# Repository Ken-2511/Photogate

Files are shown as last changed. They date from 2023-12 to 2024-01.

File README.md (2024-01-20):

# Photogate

## Background

Photogates are used to measure objects' speed or acceleration. My high school physics teacher wanted a teaching aid to demonstrate the objects' speed change. In her imagination, there are ten photogates forming a tunnel, and an object go through the photogates, and the photogates show the time of seeing the object.

## My Design Specification

Here is my design specification.

### How to Detect Object

I decided to use laser emitter and receiver to detect objects' movement. Whenever an opaque object goes through the photogate, the laser is blocked, and the laser receiver would push a signal to the microprocessor (Arduino-nano).

<div align="center">
  
  <p><i>Figure 1. Red laser</i></p>
</div>

### How to Show the Time

I installed a nixie-tube on each photogate to show their time (Figure 1) and the nixie-tube is controlled by an Arduino-nano.

<div align="center">
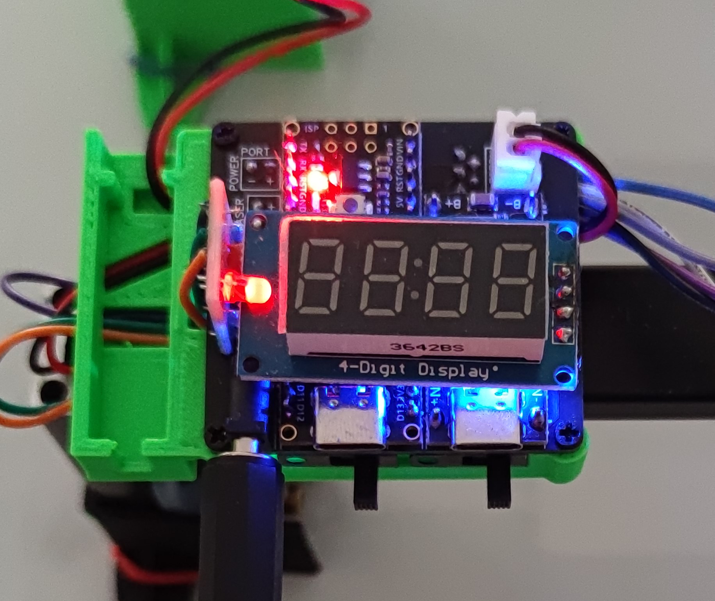
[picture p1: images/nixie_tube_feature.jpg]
  
  <p><i>Figure 2. Nixie Tube</i></p>
</div>

### How to Adjust Time

Since Arduino has no time-adjusting function, and the time-measuring job requires a very precise timing: the time error should be less than 1 millisecond. Thus, we should better not use bluetooth or WiFi to adjust time.

In this project, I used infrared remote controlling technique, similar to TV controller or AC controller.

However, the existing libraries does not fulfill our need as they are memory-consuming and low-efficient. Most libraries only support to transmit 8 bits per time. Therefore, I developed my own "protocol" to allow it transmit up to 32 bytes (256 bits) per time (they are defined in "photogate.c" and "PhotogateController.c").

There is a "photogate controller", as the name says, it controls all the ten photogates by sending infrared signals (Figure 2). We use the controller's internal timer as the "standard time", and each photogate adjust time and stores the difference between their timers into their memory. Since the time difference between each timer does not vary, we got a relatively precise timing system.

By applying this technique, we finally got the time-adjusting system with lower than 150 microseconds (0.00015 seconds) precision, which is adequate for being a teaching aid.

<div align="center">
  
  <p><i>Figure 3. Controller</i></p>
</div>

### User-Friendly Consideration

To make it usable by a non-programmer, I designed a graphoc user interface (GUI) using Python Tkinter library.

### Physical Design Specification

The overall structure is built by aluminum beams. To make it more stable (not easy to fall down), I 3D printed some kind of stands and stick it on the photogates.

This design uses many electronic devices, including voltage-boosting module, battery controlling module, switches, and nixie tube.... To integrade these electronic modules together, I designed a PCB and soldered them together. I also printed a tiny box to hold electronics and fix them to the aluminum frame.

The laser does not always accurately shoot on the laser receiver. Therefore, I designed a "fine-tuning" structure. By turning the screw, we can slightly adjust the laser's direction.

For further information, you can check the <a href="https://github.com/Ken-2511/Photogate/blob/main/%E5%85%89%E7%94%B5%E9%97%A8%E8%AF%B4%E6%98%8E%E6%89%8B%E5%86%8C.docx">.docx</a> file.

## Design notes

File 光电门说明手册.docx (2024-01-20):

# 光电门说明手册

# 材料清单：

1 U盘
2 10个光电门
3 光电门的“遥控器”
4 一个小盒子（小盒子里有：）
  a. 一些3D打印的零件，主要是怕零件损坏所以多给了几个冗余零件，绝对不是因为打印多了没处放
  b. “纳米胶”（就是那个透明的胶带。光电门上很多东西都是拿它粘的）
  c. 一个树莓派pico。原本打算用在光电门上的，结果没用上，所以就送给老师同学们玩。这可好玩了，可以做很多东西。
  d. 几个六角扳手
  e. 一小包M2自攻螺丝
  f. 一些M3螺丝和防松螺母
  g. 一些M5螺丝和滑块螺母

# 参数说明

计时精确度：通过不精确测量，光电门之间校对时间的误差≈100μs

无线传输距离：还没量过，但传输距离应当和电视机遥控器距离相当

激光扫描速度：由于激光的触发是通过中断实现的，据说IO扫描速度大约是几微秒到几十微秒不等（根据我之前测量的经验，我只能得出扫描速度在1μs到1ms之间😓）但是这个速度完全够用，即使是以20m/s的速度飞过一块橡皮，也是能被扫描到的。

# 使用方法介绍：

此光电门是用来测量物体速度的。每个门都在固件上被从0到9地编好号了，每个门都有两个开关，左边的开关是主机开关，右边的开关是充电开关。打开光电门的主机开关后，光电门的数码管会显示数字。这时需要人为地将各个光电门按照数字垂直一字排开，就像这样 “[[[[[[[[[[” 。

使用者需要使用一台电脑，使用一根TYPE-C线将T字形的遥控器与电脑连接，并打开U盘里的光电门软件（Photogate Upper Computer）。不出意外的话，光电门软件会自动检测串口，连接到遥控器。

使用者需要将遥控器地红外线发射二极管对着光电门的方向（就像使用电视机遥控器一样）。同样地，每个光电门的红外线发射二极管也应当对着遥控器的方向。此外，建议将遥控器和光电门放至同一高度，并避免在阳光直射的环境下使用设备，以达到最佳的消息传输效果。

在开始测量前，最好进行“debug laser”，确保光电门的激光检测功能正常工作。在电脑上点击“debug laser”后，光电门的激光发射器会打开，并在数码管上显示“yES”或者“no”。如果一个门在有障碍物挡住激光的时候显示no并在没有障碍物的时候显示yes，则说明这个门的激光检测装置是正常工作的。如果没有正常工作，很可能是因为激光没有对准激光接收器，这时候需要使用六角扳手拧螺丝进行微调。

当所有光电门都正常工作后，可以在电脑上点击“monitor”，这时候光电门会进入监控状态，数码管显示“----”。当光电门检测到有障碍物挡住激光的时候，会立刻关闭激光，并在数码管上显示“SEEN”。在monitor模式下，光电门只能被触发一次，然后就不会被触发了。如果出现了误触之类的状况，可以在电脑上重新点击 “monitor” 按键以重置光电门。

待所有光电门都检测完成后，电脑会向光电门收集有关时间的信息，然后将经过光电门的物体的各种信息和图像绘画出来。

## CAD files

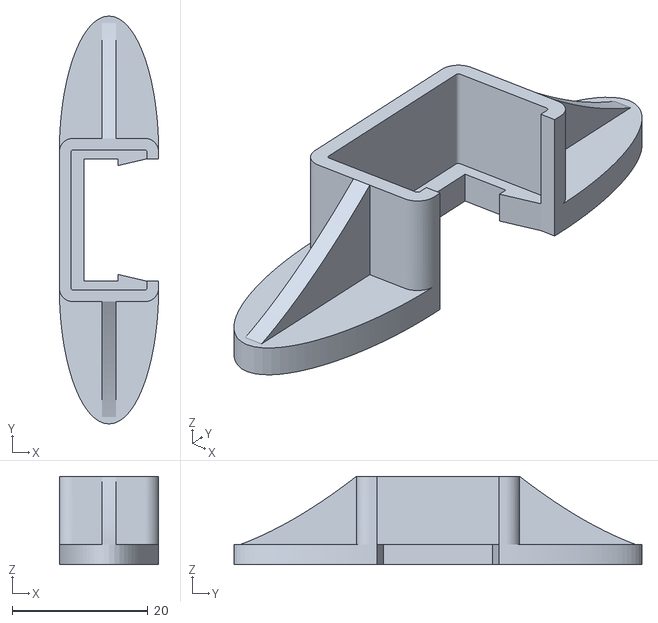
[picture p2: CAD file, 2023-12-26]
3D_models_DLP/foot1.stl
14.6 x 60.0 x 13.0

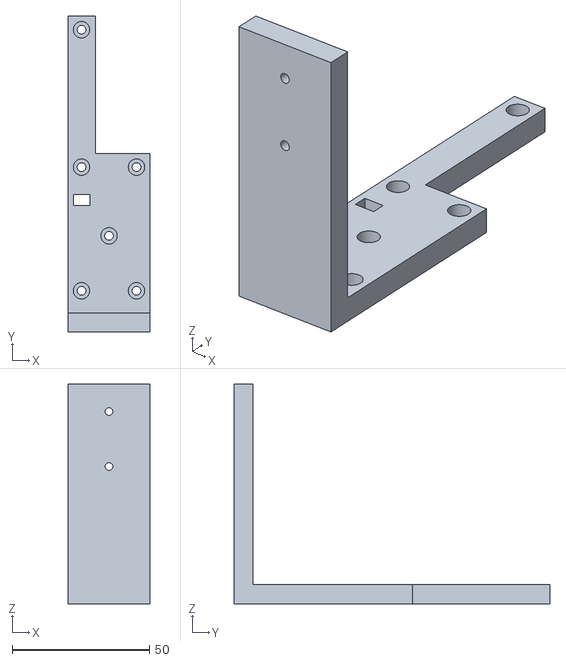
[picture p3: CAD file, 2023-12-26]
3D_models_FDM/�1.stl
30.0 x 115.0 x 80.0

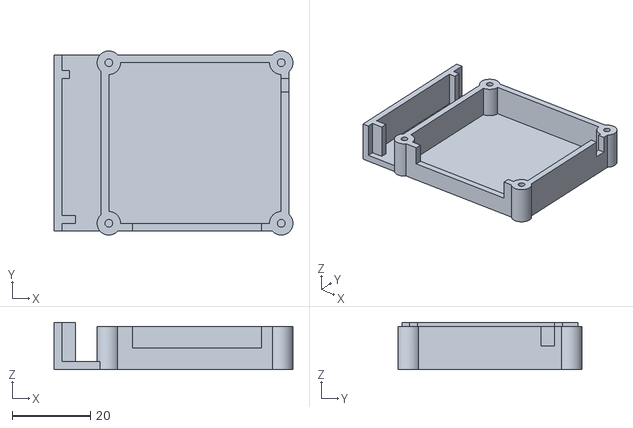
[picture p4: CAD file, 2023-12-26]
3D_models_DLP/box3.stl
61.0 x 47.0 x 12.0

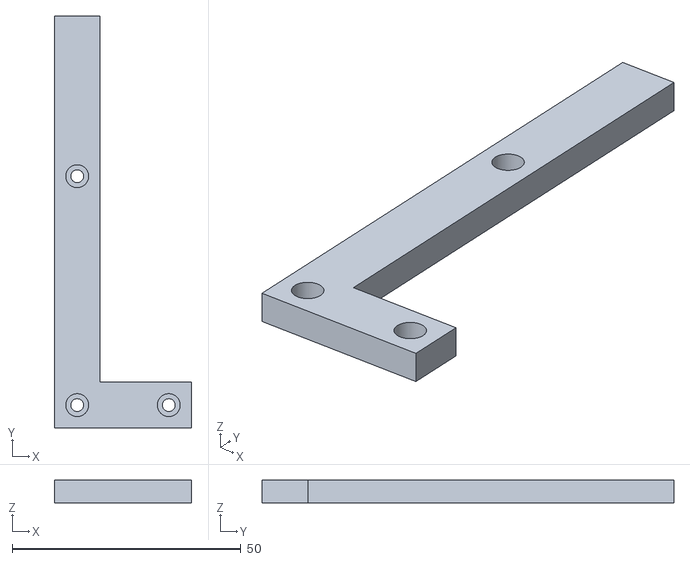
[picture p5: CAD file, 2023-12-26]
3D_models_FDM/�աɵ�1.stl
30.0 x 90.0 x 5.00

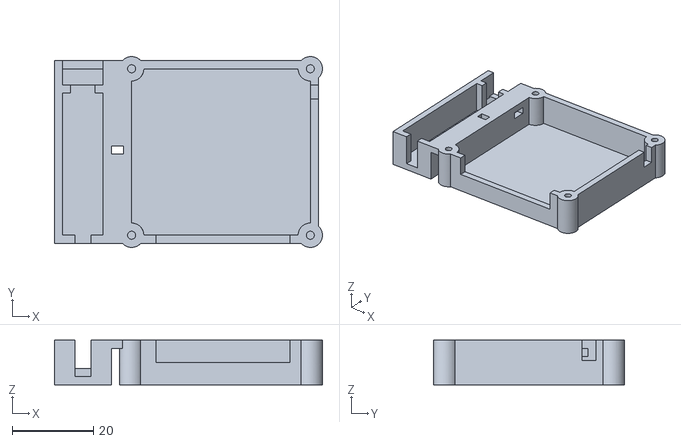
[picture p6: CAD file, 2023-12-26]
3D_models_DLP/box4.stl
66.0 x 47.0 x 11.0

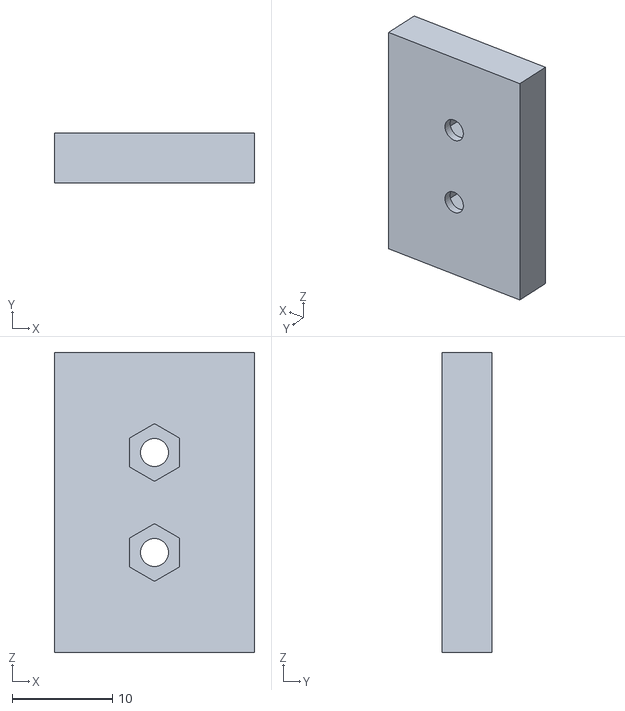
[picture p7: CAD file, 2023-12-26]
3D_models_FDM/޻�-�צ�.stl
20.0 x 5.00 x 30.0

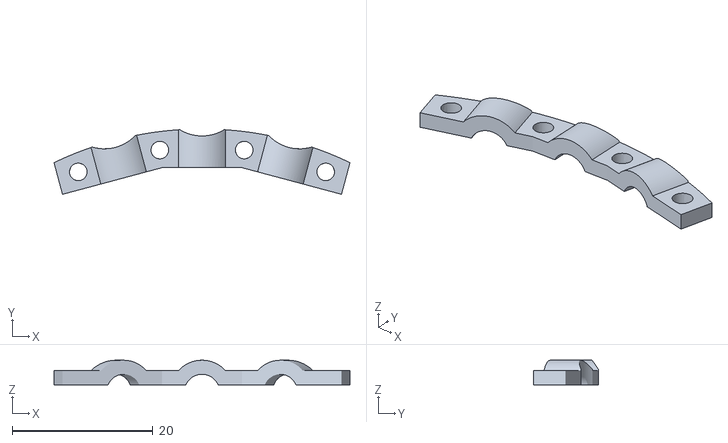
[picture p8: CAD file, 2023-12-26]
3D_models_DLP/IR_frame3.stl
42.1 x 9.19 x 3.50

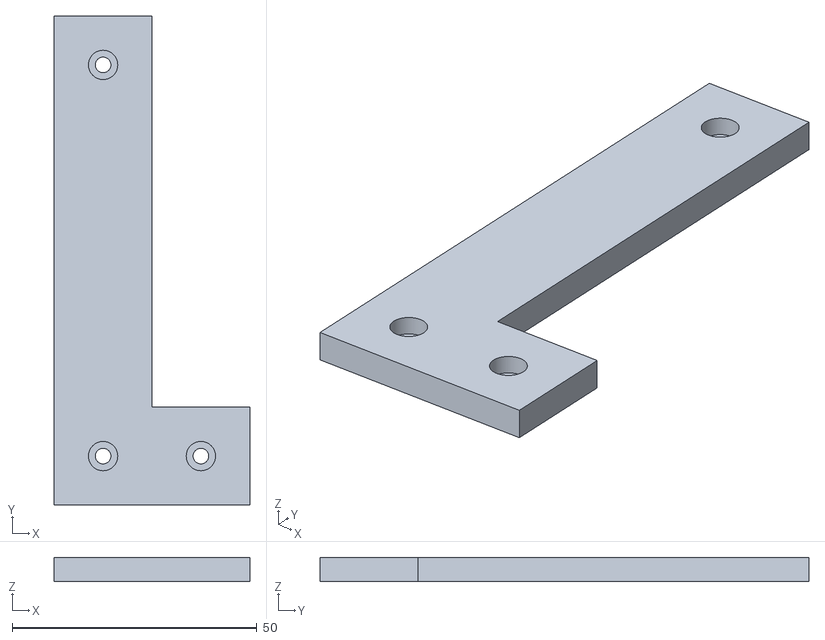
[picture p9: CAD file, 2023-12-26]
3D_models_FDM/�ա�զ�զ�.stl
40.0 x 100.0 x 5.00

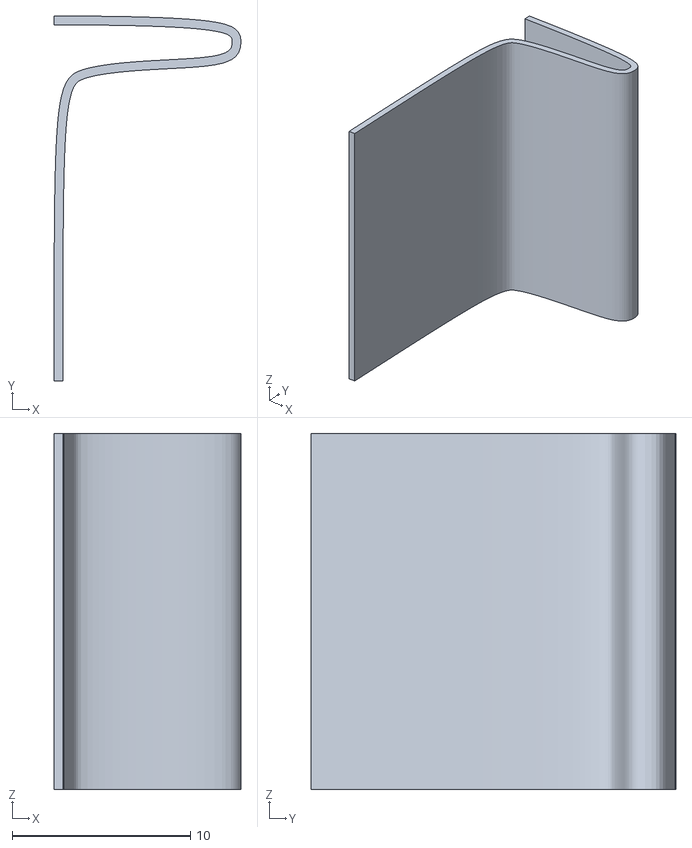
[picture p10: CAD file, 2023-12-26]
3D_models_DLP/laser_frame_test2.stl
10.5 x 20.5 x 20.0

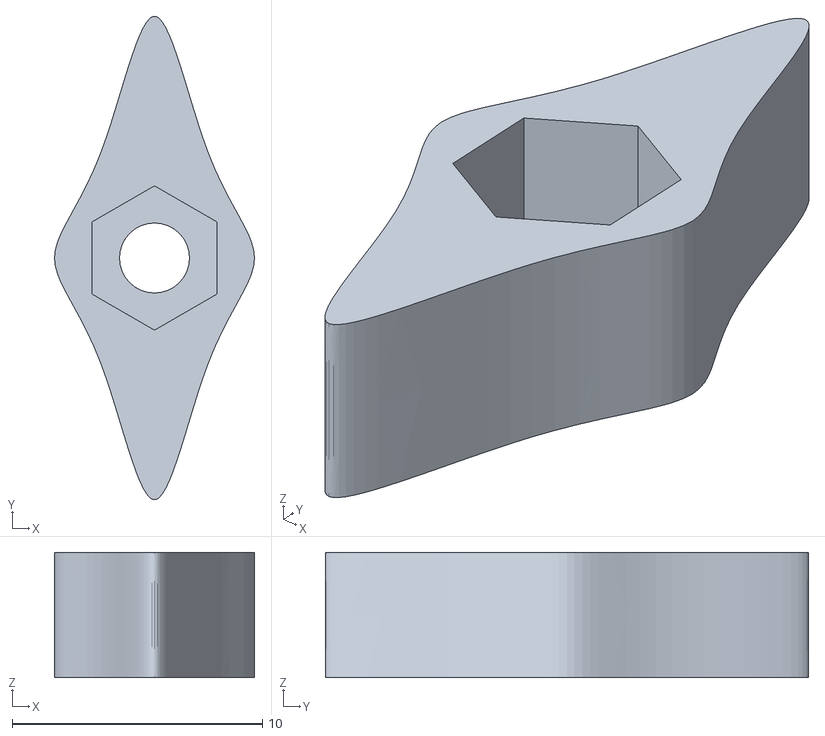
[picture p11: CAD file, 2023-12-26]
3D_models_FDM/�צ�1.stl
8.00 x 19.3 x 5.00

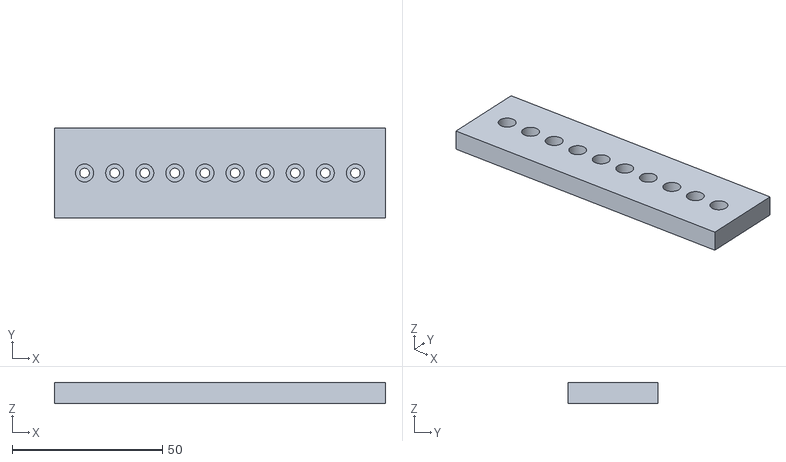
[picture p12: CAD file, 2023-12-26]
3D_models_FDM/�+׵�ѵ�.stl
110.0 x 30.0 x 7.00

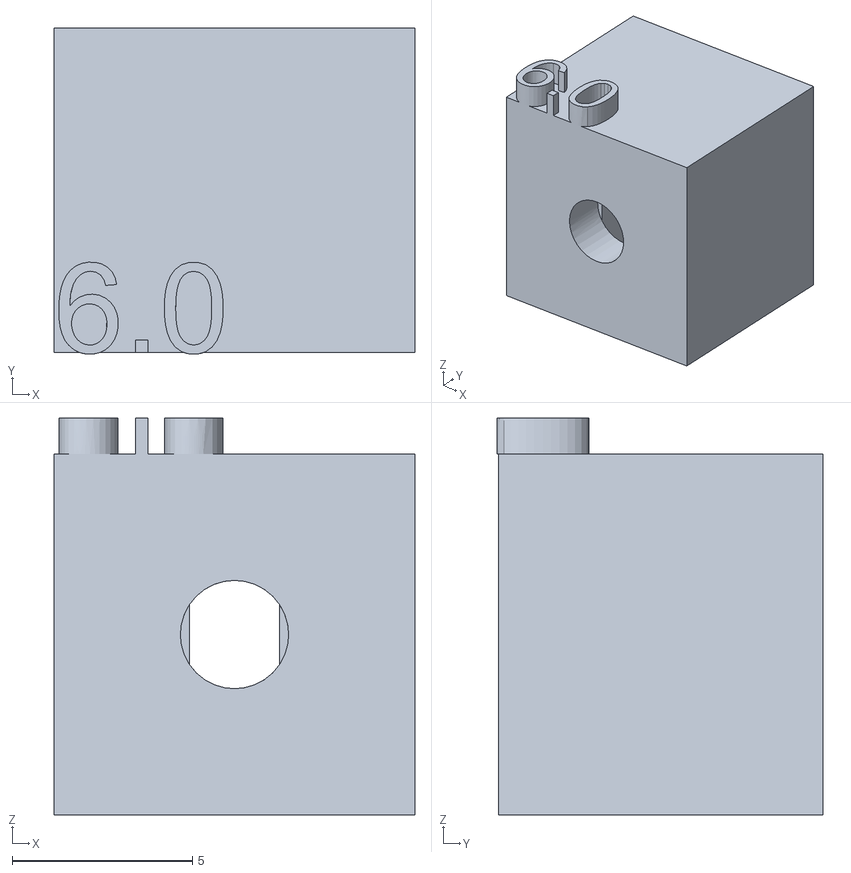
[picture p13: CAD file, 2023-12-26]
3D_models_DLP/laser_frame_test5.stl
10.0 x 9.04 x 11.0

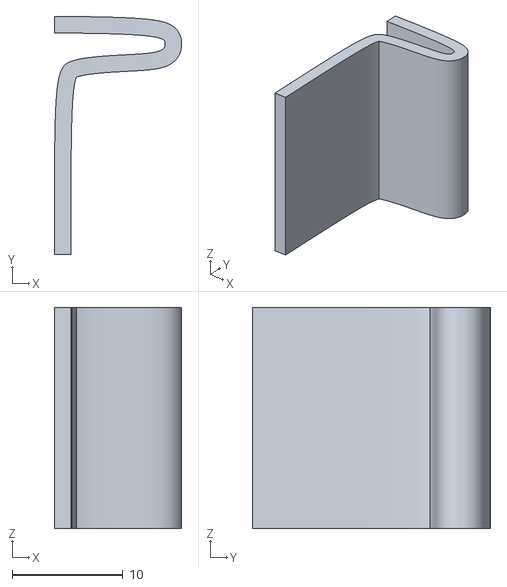
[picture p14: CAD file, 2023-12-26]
3D_models_DLP/laser_frame_test.stl
11.5 x 21.5 x 20.0

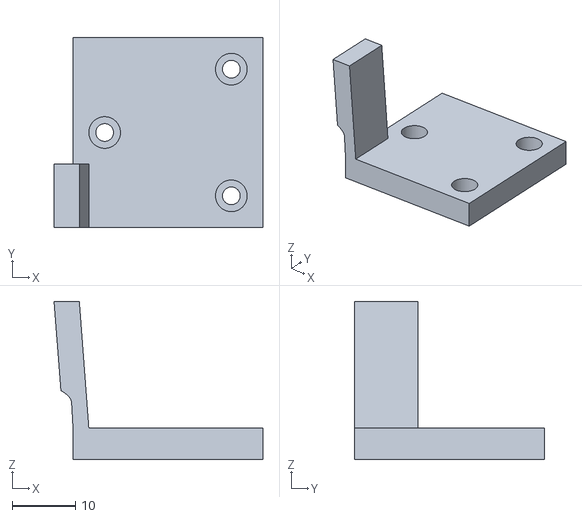
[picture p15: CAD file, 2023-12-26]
3D_models_FDM/�+�.stl
33.0 x 30.0 x 25.0

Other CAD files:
3D_models_DLP/box5.stl
3D_models_FDM/��աɵ�����2.stl
3D_models_DLP/box1.stl
3D_models_FDM/�2.stl
3D_models_DLP/IR_frame.3dm
3D_models_DLP/IR_frame.stl
3D_models_DLP/IR_frame1.3dm
3D_models_DLP/IR_frame1.stl
3D_models_DLP/IR_frame2.3dm
3D_models_DLP/IR_frame2.stl
3D_models_DLP/box.stl
3D_models_DLP/box2.stl
3D_models_DLP/box6.stl
3D_models_DLP/circuit_board_kit.3dm
3D_models_DLP/circuit_board_kit_1.3dm
3D_models_DLP/circuit_board_kit_2.3dm
3D_models_DLP/circuit_board_kit_3.3dm
3D_models_DLP/foot.3dm
3D_models_DLP/foot.stl
3D_models_DLP/joint.3dm
3D_models_DLP/joint.stl
3D_models_DLP/joint1.stl
3D_models_DLP/laser_frame.3dm
3D_models_DLP/laser_frame1.3dm
3D_models_DLP/laser_frame2.3dm
3D_models_DLP/laser_frame_test1.stl
3D_models_DLP/laser_frame_test3.stl
3D_models_DLP/laser_frame_test4.stl
3D_models_DLP/laser_frame_test6.stl
3D_models_DLP/laser_frame_test7.stl
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

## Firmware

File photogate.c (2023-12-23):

/*
这是程永康写的放在光电门上的程序，写得可能有点草率/不标准，请多多见谅
作为一个C语言小白，程永康边学边写，问了ChatGPT好多问题……
我会尽量多写注释的，希望你能看懂。
*/

#include <limits.h>
#include <TM1637Display.h>

#define iremt 7       // infrared emit 红外发射引脚
#define irrcv 3       // infrared receive
#define lsemt 6       // laser emit
#define lsrcv 2       // laser receive
#define ir_maxlen 32  // 红外线通讯时接收信号的最大长度
#define nixie_clk 5   // 数码管的时钟线
#define nixie_dio 4   // 数码管的数据线
#define battery 0

unsigned long time_stamp;    // 这个变量保存着每个函数开始/结束的时间，或者是一些重要的时间戳
char receive_buffer[ir_maxlen] = {0};
char send_buffer[ir_maxlen] = {0};      // 这是发送端的缓冲区
char message_buffer[ir_maxlen-2] = {0};
char _send_buffer[ir_maxlen] = {0};
char id = '0';

TM1637Display display = TM1637Display(nixie_clk, nixie_dio);

// ########################################################
// 以下是红外线发送的相关函数

void send_BOF() {
  time_stamp = micros();
  time_stamp += 5000;
  while (micros() < time_stamp) {
    digitalWrite(iremt, HIGH);
    delayMicroseconds(5);
    digitalWrite(iremt, LOW);
    delayMicroseconds(15);
  }
  time_stamp += 5000;
  while (micros() < time_stamp);
}

void send_bit(bool data) {
  // 先发送500微秒高频信号
  time_stamp += 500;
  while (micros() < time_stamp) {
    digitalWrite(iremt, HIGH);
    delayMicroseconds(5);
    digitalWrite(iremt, LOW);
    delayMicroseconds(15);
  }
  // 静默一定时间：0 = 500, 1 = 1000
  if (data)
    time_stamp += 1000;
  else
    time_stamp += 500;
  while (micros() < time_stamp);
}

void send_EOF() {
  // 发送1000毫秒的高频脉冲
  time_stamp += 1000;
  while (micros() < time_stamp) {
    digitalWrite(iremt, HIGH);
    delayMicroseconds(5);
    digitalWrite(iremt, LOW);
    delayMicroseconds(15);
  }
}

void send() {
  static size_t i;
  static int bit_pos;
  static char c;
  static bool b;
  // 先encode
  size_t length = encode();
  // 先发送开始位
  send_BOF();
  // 再发送消息内容
  for (i=0; i<length; i++) {
    c = _send_buffer[i];
    for (bit_pos=7; bit_pos>=0; bit_pos--) {
      b = (c >> bit_pos) & 1;
      send_bit(b);
    }
  }
  // 再发送结束位
  send_EOF();
}

// ########################################################
// 以下是红外线接收的相关函数

bool check_ir() {
  // 检测是否看见了红外信号
  static unsigned long last_high = 0;   // 上次检测到高电平的时间
  static unsigned long now;
  static unsigned long timeout;
  now = micros();
  // 现在如果是高电平，肯定不符合条件的，就直接返回false
  if (digitalRead(irrcv)) {
    last_high = now;
    return false;
  }
  // 检查现在是否在10ms区间内，只有在10ms区间内才符合要求。（有1ms模糊判定）
  if ((now - last_high < 4000) | (now - last_high > 6000)) {
    return false;
  }
  // 以下是在10ms区间内的情况
  timeout = now + 2000;
  while (!digitalRead(irrcv)) {   // 等待变成高电平
    // 如果超时就返回false
    if (micros() > timeout)
      return false;
  }
  // 以下是在5ms区间内的情况
  timeout = micros() + 6000;
  while (digitalRead(irrcv)) {
    // 如果超时就返回false
    if (micros() > timeout)
      return false;
  }
  time_stamp = micros();
  return true;
}

int receive_bit() {
  static unsigned long duration;
  static unsigned long timeout;
  // 接收一个bit。返回内容：0=0, 1=1, 2=EOF,-1=ERROR
  // 有250μs的时间容忍度
  // 当前是低电平，等待500μs/1000μs的小波过去
  timeout = time_stamp + 1250;
  while (!digitalRead(irrcv)) {
    if (micros() > timeout)
      return -1;
  }
  // 如果脉冲时间是1000μs，说明是EOF
  duration = micros() - time_stamp;
  if (duration > 750)
    return 2;
  if (duration < 250)
    return -1;
  // 当前是高电平，通过高电平的时间判断发送的是何种数据
  // 500μs=0, 1000μs=1
  time_stamp = micros();
  timeout = time_stamp + 1250;
  while (digitalRead(irrcv)) {
    if (micros() > timeout)
      return -1;
  }
  // 开始判断接收到的是何种数据
  duration = micros() - time_stamp;
  time_stamp = micros();
  if (duration > 750)
    return 1;
  if (duration > 250)
    return 0;
  return -1;
}

int receive() {
  // 接收raw data，成功返回字符数，不成功返回0
  // 这里的前提条件是刚刚检测到了红外信号的开端
  static size_t buf_len;
  static int bit_pos;
  static char c;
  static int b;
  memset(receive_buffer, 0, ir_maxlen);   // 将buffer清空
  for (buf_len=0; buf_len<ir_maxlen; buf_len++) {
    c = 0;
    for (bit_pos=7; bit_pos>=0; bit_pos--) {
      b = receive_bit();
      if (b == -1)    // 如果这个子函数报错了，那就报错
        return 0;
      if (b == 2)     // 如果收到了结束信号（EOF），就返回
        return buf_len;
      // 走到这说明正常收到了一个bit
      // 将收到的bit存到字符串中
      c |= b << bit_pos;
    }
    receive_buffer[buf_len] = c;
  }
  return 0;   // 这里超出buffer的范围了也是要报错的
}

/*以下是各种各样的命令，这些命令是红外线/串口调用的
每当处理器接收到一个command，主程序会循环调用这些函数，并传入参数`command`
`command`是一个字符串。如果command里的第一个单词与函数里的密令是一样的，
就说明command就是想要调用这个函数。*/

int control_laser(char* command)
// 命令：控制激光灯的亮灭
{
  if (!strcmp(command, "ON"))
  {
    digitalWrite(lsemt, HIGH);
    return 0;
  }
  if (!strcmp(command, "OFF"))
  {
    digitalWrite(lsemt, LOW);
    return 0;
  }
  return -1;
}

unsigned long laser_seen_time = 0;;
bool laser_seen = false;
void laser_interrupt()
// 激光触发的中断程序，只能触发一次
{
  if (laser_seen)
    return;
  laser_seen_time = micros();
  laser_seen = true;
  digitalWrite(lsemt, LOW);
  uint8_t segment[4] = {0x6d, 0x79, 0x79, 0x37};
  display.setSegments(segment);
}

int monitor(char* command)
// 命令：开始/停止监测激光
{
  if (!strcmp(command, "ON"))
  {
    digitalWrite(lsemt, HIGH);
    uint8_t segment[4] = {64, 64, 64, 64};
    display.setSegments(segment);
    delay(50);
    detachInterrupt(digitalPinToInterrupt(lsrcv));
    attachInterrupt(digitalPinToInterrupt(lsrcv), laser_interrupt, RISING);
    laser_seen = false;
    return 0;
  }
  if (!strcmp(command, "OFF"))
  {
    detachInterrupt(digitalPinToInterrupt(lsrcv));
    digitalWrite(lsemt, LOW);
    display.clear();
    return 0;
  }
  return -1;
}

void laser_debug_interrupt() {
  static uint8_t yes[4] = {0, 110, 121, 109};
  static uint8_t no[4] = {0, 0, 84, 92};
  if (digitalRead(lsrcv))   // means can not see
    display.setSegments(no);
  else
    display.setSegments(yes);
}

int debug_laser(char* command)
{
  if (!strcmp(command, "ON")) {
    digitalWrite(lsemt, HIGH);
    detachInterrupt(digitalPinToInterrupt(lsrcv));
    attachInterrupt(digitalPinToInterrupt(lsrcv), laser_debug_interrupt, CHANGE);
    laser_debug_interrupt();
    return 0;
  }
  if (!strcmp(command, "OFF")) {
    digitalWrite(lsemt, LOW);
    detachInterrupt(digitalPinToInterrupt(lsrcv));
    display.clear();
    return 0;
  }
  return -1;
}

int check_laser()
// 命令：检查激光是否检测到有物品经过
{
  if (laser_seen)
  {
    strcpy(send_buffer, "true");
  } else {
    strcpy(send_buffer, "false");
  }
  return 0;
}

int tell_time()
// 命令：汇报激光检测到物品的时间
{
  sprintf(send_buffer, "%lu", laser_seen_time);
  return 0;
}

int adjust_time()
{
  sprintf(send_buffer, "%lu", micros());
  return 0;
}

int tell_voltage()
{
  sprintf(send_buffer, "%d", analogRead(battery));
  return 0;
}

char nixie_segment[4];
int set_segment(char* command)
{
  uint8_t segment[4];
  for (int i=0; i<4; i++) {
    if (command[i] == ' ')
      command[i] = '\0';
    segment[i] = (uint8_t)(command[i]);
  }
  display.setSegments(segment);
  return 0;
}

int set_brightness(char* command)
{
  if (strlen(command) != 1)
    return -1;
  char* endptr;
  unsigned long result;
  result = strtoul(command, &endptr, 10);
  if (result > 7)
    return -1;
  display.setBrightness((uint8_t)result);
  return 0;
}

int set_number_colon(char* command) {
  if (strlen(command) != 4)
    return -1;
  for (int i=0; i<4; i++) {
    if (!isdigit(command[i]))
      return -1;
  }
  char *endptr;
  int num = (int)strtoul(command, &endptr, 10);
  Serial.println(num);
  display.showNumberDecEx(num, 64);
  return 0;
}

int are_you_ok(char* command) {
  if (strlen(command) != 0)
    return -1;
  return 0;
}

void _print(char* command)
// 开发使用的函数，打印出字符串里的0和1
{
  Serial.print("print...[");
  Serial.print(command);
  Serial.print("]: ");
  for (int i=0; i<ir_maxlen; i++)
    {
      Serial.print(command[i]);
      for (int j=7; j>=0; j--)
      {
        Serial.print(command[i] >> j & 1);
      }
      Serial.print(" ");
    }
    Serial.println();
}

/*给定字符串，根据字符串调用合适的函数*/
void process_command(char* command)
{
  // 准备send_buffer，默认是`ok`
  memset(send_buffer, 0, ir_maxlen);
  strcpy(send_buffer, "ok");
  // token是第一个单词，rest是剩下的部分
  char temp[ir_maxlen];
  strcpy(temp, command);
  char *token, *rest = temp;
  token = strsep(&rest, " ");
  int result;
  if (!strcmp(token, "LSR")) {            // laser
    result = control_laser(rest);
  } else if (!strcmp(token, "MNT")) {     // monitor
    result = monitor(rest);
  } else if (!strcmp(token, "CHKL")) {    // check laser
    result = check_laser();
  } else if (!strcmp(token, "TLTM")) {    // tell time
    result = tell_time();
  } else if (!strcmp(token, "ADJT")) {    // adjust time
    result = adjust_time();
  } else if (!strcmp(token, "NXB")) {     // nixie brightness
    result = set_brightness(rest);
  } else if (!strcmp(token, "NXS")) {     // nixie set segment
    result = set_segment(rest);
  } else if (!strcmp(token, "NXN")) {     // nixie set number
    result = set_number_colon(rest);
  } else if (!strcmp(token, "TLV")) {     // tell voltage
    result = tell_voltage();
  } else if (!strcmp(token, "DBL")) {     // debug laser
    result = debug_laser(rest);
  } else if (!strcmp(token, "RUOK")) {    // check whether alive
    result = are_you_ok(rest);
  } else {
    result = -1;
  }
  if (result == -1) {
    strcpy(send_buffer, "BAD CMD");
  }
}

int decode(int r_buf_length) {
  // 将receive buffer里的内容进行校对，将有用的信息转到message buffer里
  // 成功返回0，发现id不对或者校验失败，就返回-1
  // 先进行xor校验
  // 因为消息的最后一位是校验位，所以校验位最后会xor自己，
  // 所以在接收正确的情况下xor checker应该等于零
  char xor_checker = 0;
  for (int i=0; i<r_buf_length; i++) {
    xor_checker ^= receive_buffer[i];
  }
  if (xor_checker)
    return -1;
  // 检查消息发送的id是否是自己的id
  // 换言之检查这个消息是不是给自己发送的
  char message_id = receive_buffer[0];
  if (message_id != id)
    return -1;
  // 将消息转存到message buffer里
  memset(message_buffer, 0, ir_maxlen-2);
  strcpy(message_buffer, receive_buffer+2);
  return 0;
}

size_t encode() {
  // 接下来是给字符串编码的函数
  // 将send_m_buff里的内容加入校验位并转存到send_buffer里
  _send_buffer[0] = 0;    // 因为主控的id是0，光电门肯定是给主控发消息
  strcpy(_send_buffer+1, send_buffer);
  // 开始计算校验位，使用XOR校验
  char xor_checker = 0;
  size_t s_buf_len = strlen(send_buffer) + 2;    // 加了一个'\0'
  for (size_t i=0; i<s_buf_len; i++) {
    xor_checker ^= _send_buffer[i];
  }
  _send_buffer[s_buf_len] = xor_checker;
  return ++s_buf_len;                               // 再加一个校验位
}

void setup() {
  pinMode(iremt, OUTPUT);
  pinMode(irrcv, INPUT);
  pinMode(lsemt, OUTPUT);
  Serial.begin(9600);
  display.setBrightness(7);
  display.showNumberDec(atoi(&id));
}

void loop() {
  // 等待接收
  if (!check_ir())
    return;
  int r_num = receive();
  if (!r_num)
    return;
  if (decode(r_num))
    return;
  process_command(message_buffer);
  // 等待一定时间回复
  delay(10);
  send();
  Serial.println(send_buffer);
}
